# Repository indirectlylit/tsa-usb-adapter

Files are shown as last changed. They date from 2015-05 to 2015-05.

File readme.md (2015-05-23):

# TSA-to-USB Adapter

This project allows computers to communicate with the [Medoc TSA II](http://www.medoc-web.com/products/tsa-ii) using a serial protocol sent over a USB port.

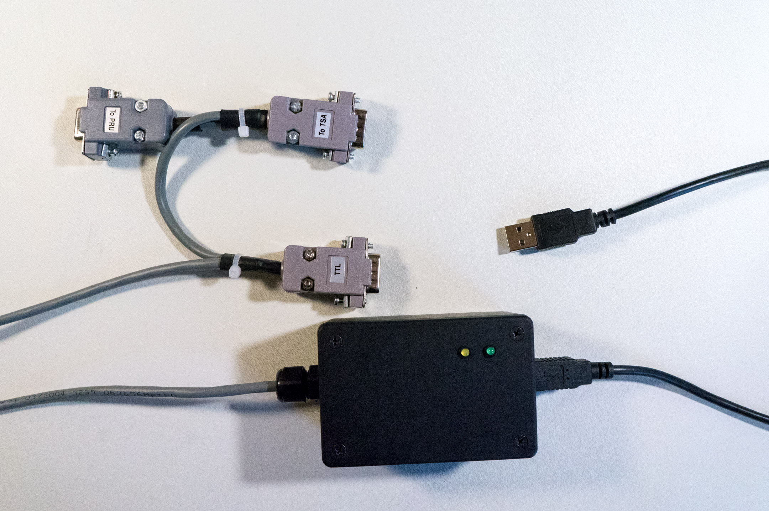
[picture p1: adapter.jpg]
adapter Adapter


## Quick-start

You should also read the the TSA II operation manual (TSA2OperationManual.pdf) to learn how to build TSA programs that send and receive TTL signals.

### Setup

**OSX and Linux**

Plug the adapter into the computer with a USB cord. You may initially get prompts to set up a keyboard or a networking device. Accept the changes and you shouldn't be prompted again.

To verify that the device is available:

* Open the Terminal
* run `ls /dev | grep usb`
* this should return one tty port, for example `/dev/tty.usbmodem411`.

**Windows**

Plug the adapter into the computer with a USB cord. In tests on Windows 7, the computer automatically searched for and installed drivers with no additional work needed.

To verify that the device is available:

* Open the Device Manager
* Look for an entry in the tree: Ports (COM & LPT) > Arduino Micro (COM*N*)

If the drivers did not install successfully in the prior step, you may need to install them manually. For help, try following [these instructions](https://learn.sparkfun.com/tutorials/pro-micro--fio-v3-hookup-guide#installing-windows).

### TSA Software

Open the Hardware Settings dialog in the TSA software to make sure communication is working. Here you can send and receive test pulses.

*NOTE - While the Medoc TSA purports to accept TTL pulse inputs, we have not been able to get it to work.*

### LED feedback

* plug in to computer - green LED will turn on
* `connect()` from the computer - green LED will flash once
* `trigger()` a TTL pulse from the computer - yellow LED will flash once
* receive a TTL pulse from the TSA - yellow LED will flash twice

## Programming in MATLAB

Note that MATLAB will not see the adapter unless it is plugged in when MATLAB starts.

You'll need access to *matlab/TSAAdapter.m* in your program.

### API

**`tsa = TSAAdapter()`**

Constructor - returns a new TSA object. This only needs to be done once at the beginning of your program.

**`tsa.connect()`**

Establish a connection with the adapter. This only needs to be done once at the beginning of your program.

**`tsa.trigger()`**

Send a TTL pulse to the TSA. *NOTE - While the Medoc TSA purports to accept TTL pulse inputs, we have not been able to get it to work.*

**`tsa.check()`**

Return `1` (true) if a TTL pulse was sent by the TSA since the last time `check()` was called; return `0` (false) otherwise. If multiple pulses are sent, `check()` will still only return a `1`.

**`tsa.disconnect()`**

Drop the connection with the adapter. This is optional, as the connection will be automatically dropped when your script ends.

### Example

Basic usage is as follows:

```
>> tsa = TSAAdapter()
>> tsa.connect()
>> tsa.trigger()  % sends a pulse to the TSA
>> tsa.check()    % has a pulse been received since last check?
false
>> tsa.check()
false
>> tsa.check()
true
>> tsa.check()
false
>> tsa.disconnect()
```

## Programming in Python

These notes only apply if you're writing a program in Python - not MATLAB.

The Python helper requires `pyserial` to be installed. This can be obtained by running `pip install pyserial` from the command-line.

You'll need to import the *python/tsa.py* file into your program.

### API

**`import tsa`**

Import the TSA module. This only needs to be done once at the beginning of your program.

**`tsa.connect()`**

Establish a connection with the adapter. This only needs to be done once at the beginning of your program.

**`tsa.trigger()`**

Send a TTL pulse to the TSA.

*NOTE - While the Medoc TSA purports to accept TTL pulse inputs, we have not been able to get it to work.*

**`tsa.check()`**

Return `True` if a TTL pulse was sent by the TSA since the last time `check()` was called; return `False` otherwise. If multiple pulses are sent, `check()` will still only return `True`.

**`tsa.wait()`**

Block execution until a TTL is sent by the TSA.

**`tsa.disconnect()`**

Drop the connection with the adapter. This is optional, as the connection will be automatically dropped when your script ends.

### Example

Basic usage is as follows:

```
>>> import tsa
>>> tsa.connect()
>>> tsa.trigger()  # sends a pulse to the TSA
>>> tsa.wait()     # this call will block until a pulse is received
True
>>> tsa.check()    # has a pulse been received since last check?
False
>>> tsa.check()
False
>>> tsa.check()
True
>>> tsa.check()
False
>>> tsa.disconnect()
```

## Implementation Details

### Theory of Operation

The TSA can send and receive signals via very simple pulses of electricity, called TTL signals. For example, a pulse could signal the TSA to start a test, or the TSA could send a pulse when the user clicks the mouse. Refer to the TSA operation manual (TSA2OperationManual.pdf) for more information on creating TSA programs that send and receive pulses.

Most personal computers do not have the ability to use raw TTL pulses, so this adapter was made to allow programs (e.g. MATLAB or Python) to interact with the TSA. The adapter works by translating TTL signals to serial port messages and vice-versa. The serial port messages are then sent over a USB cable to the computer.

### Serial Protocol

The MATLAB and Python helper libraries implement the logic described below. However, you may be interested in implementing the logic differently; for example if more precise timing is required, then it might be implemented inside a thread (Python) or using event-driven callbacks (MATLAB). It can also be implemented in another programming language.

With the adapter plugged into the computer, have your program or terminal program open a serial port on `/dev/tty.usbmodem411` at 9600 bps.

The adapter communicates with the computer via a simple pair of messages:

* To instruct the adapter to send a pulse to the TSA, send a `*` character over the serial port from the computer.
* When the TSA sends a pulse, a `#` character will be sent from the adapter to the computer over the serial port.

Writing programs to read and write serial port messages is straightforward, and libraries are available in most languages. You can also use a serial terminal program like [CoolTerm](http://freeware.the-meiers.org/) or [screen](https://embeddedfreak.wordpress.com/2008/08/12/using-gnu-screen-to-debug-your-serial-port/) to experiment with the serial port without writing any code.

### Hardware

The adapter is built around an Arduino-compatible microprocessor board, the [SparkFun Pro Micro](https://www.sparkfun.com/products/12640). More information about how it's put together is contained in the *hardware* directory and the *readme.md* file there.

## Copyright

Written and built by Devon Rueckner for [Carissa Cascio at the Vanderbilt University Medical Center](http://www.casciolab.com/).

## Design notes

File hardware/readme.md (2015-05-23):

# Files

* *model.skp* is a [Sketchup](http://www.sketchup.com/) file, used to find dimensions and locations for the board and enclosure cutouts. *model.pdf* is an export of this file.
* *schematic.fzz* is a [Fritzing](http://fritzing.org/) file with the circuit schematic. *schematic.pdf* is an export of this file.
* *firmware.ino* is a text file containing the source code. It can be uploaded to the chip over USB using either the [Arduino IDE](http://arduino.cc/en/main/software) or from the command line using [Ino](http://inotool.org/).
* *bom.pdf* is the bill of materials.

# Circuit notes

The following components are not included in the schematic:

1. The USB receptacle's metal shielding is connected to ground through a 1MΩ resistor and a 10nF capacitor.
2. Another capacitor is placed between Gnd and Vcc.

Also, note that the resistors and capacitors are not included in the bill of materials.

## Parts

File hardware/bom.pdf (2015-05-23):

Quantity | Part | Desc
| Mouser
1 | 645-558-0201-003F | Green LED
1 | 645-558-0301-003F | Yellow LED
2 | 538-22-23-2021 | 2-pos Male Header
1 | 538-22-23-2031 | 3-pos Male Header
1 | 538-22-23-2041 | 4-pos Male Header
2 | 538-50-57-9502 | 2-pos Female Cnctr
1 | 538-50-57-9503 | 3-pos Female Cnctr
1 | 538-50-57-9504 | 4-pos Female Cnctr
1 | 38-08-50-0113-CT | 100x crimp terminals
1 | 523-MUSBD11130 | Panel-mount USB-B
1 | 546-1591XXLBK | Enclosure
also, various resistors & capacitors; see schematic.pdf and readme.md
| SparkFun
1 | 12640 | Pro Micro - 5V/16MHz
2 | 115 | Female headers
2 | 116 | Male headers
1 | 13244 | 6" USB Micro-B Cable
1 | 512 | 6' USB A to B Cable
1 | 08619 | ProtoBoard
| McMaster-Carr
1 | 69915K47 | Cable Gland
2 | 91249A107 | Machine screw
2 | 92295A100 | Thread-forming screw

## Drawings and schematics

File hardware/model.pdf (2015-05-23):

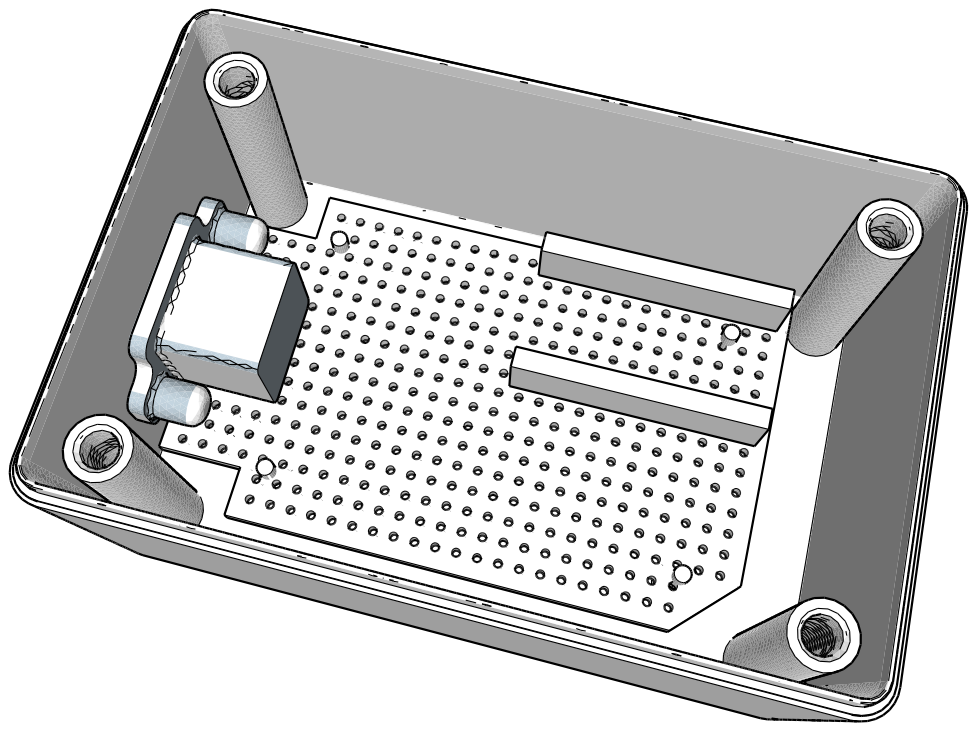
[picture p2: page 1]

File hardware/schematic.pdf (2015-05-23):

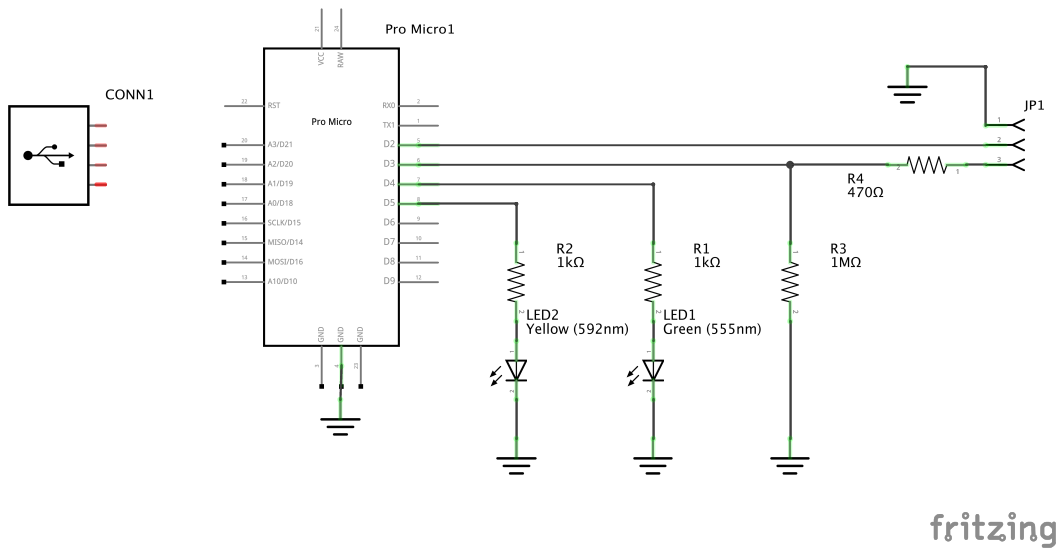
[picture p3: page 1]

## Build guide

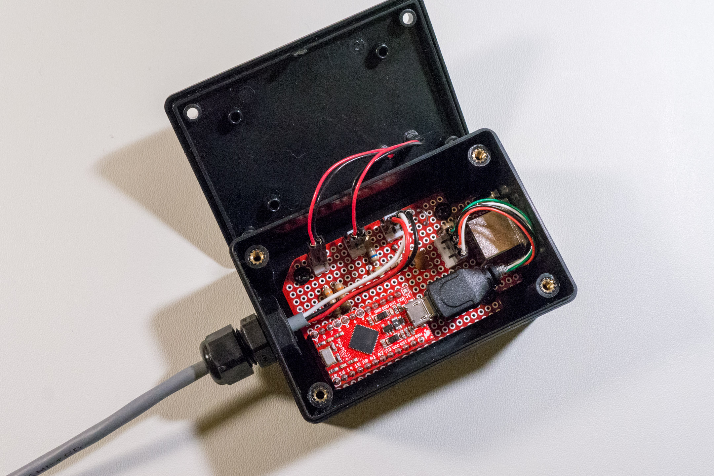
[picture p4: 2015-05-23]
hardware/assembly.jpg

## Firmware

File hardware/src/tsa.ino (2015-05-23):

/*
 *** USAGE
 *
 * This program provides a serial interface adapter to the Medoc TSA-II.
 *
 * When connected to a serial port, it will communicate at 9600 baud.
 * To instruct the TSA to start, send a single '*' character (with no line break).
 * To receive output from the TSA, listen for a '#' character.
 *
 * The status LED will blink:
 *  - 4x when the device first starts
 *  - 3x when the TSA was instructed to start
 *  - 2x when output was received from the TSA
 *  - 1x if an unknown command or character is received
 *
 *
 *** NOTES
 *
 * See the Medoc TSA-II FAQ (http://www.medoc-web.com/support/faq)
 *
 *  TTL input option:
 *    The TSA can be started by an external ±5V, 100-2000msec trigger.
 *    The trigger must be set to External in the CoVAS program algorithm.
 *
 *  TTL output option:
 *    TTL output is a ±5V, duration 50-3000msec pulse (set via Utility-»Setup).
 *    TTL output must be enabled in the CoVAS program algorithm.
 *
 * The '±' part is probably an error.
 *
 *
 *** COPYRIGHT
 *
 * Written by Devon Rueckner for Carissa Cascio
 * Vanderbilt University Medical Center
 * 2015
 *
 */


// I/O pins
#define TSA_OUTPUT_PIN  2  // to TSA-II TTL Out
#define TSA_INPUT_PIN   3  // to TSA-II TTL In
#define STATUS_PIN      4  // green LED indicator
#define ACTIVITY_PIN    5  // yellow LED indicator

// magic character for signaling
#define TRIGGER_CHAR    '#'
#define CONNECT_CHAR    '!'

// `setup` runs once when you press reset or power on.
void setup() {
    // initialize
    pinMode(TSA_OUTPUT_PIN, INPUT);
    pinMode(TSA_INPUT_PIN, OUTPUT);
    pinMode(STATUS_PIN, OUTPUT);
    pinMode(ACTIVITY_PIN, OUTPUT);
    Serial.begin(9600);

    // indicate a successful initialization
    digitalWrite(STATUS_PIN, HIGH);
}

// `receivedPulse` returns true only for a 50-3000ms pulse
bool receivedPulse() {
    unsigned long start = millis();

    do {
        // check if the pulse has ended
        if (!digitalRead(TSA_OUTPUT_PIN)) {
            // make sure the pulse was longer than 50ms
            return millis() - start > 50;
        }
    } while (millis() - start < 3000);

    // the pulse lasted longer than 3000ms
    // wait for the pulse to end and return.
    while(digitalRead(TSA_OUTPUT_PIN));
    return false;
}

// `sendTriggerPulse` sends a 200ms pulse to the TSA
void sendTriggerPulse() {
    digitalWrite(TSA_INPUT_PIN, HIGH);
    delay(200);
    digitalWrite(TSA_INPUT_PIN, LOW);
}

// `blink` flashes an LED n times
void blink(int pin, int nBlinks, bool leaveOn) {
    for (int i = 0; i < nBlinks; i++) {
        digitalWrite(pin, HIGH);
        delay(200);
        digitalWrite(pin, LOW);
        delay(200);
    }
    digitalWrite(pin, leaveOn);
}

// `loop` runs repeatedly
void loop() {

    // check if the TSA appears to be sending a signal
    if (digitalRead(TSA_OUTPUT_PIN)) {
        // wait for the pulse to end
        bool pulsed = receivedPulse();
        // if we got a valid pulse, send a signal back
        if (pulsed) {
            Serial.print(TRIGGER_CHAR);
            blink(ACTIVITY_PIN, 2, false);
        }
    }

    // check if we received a start command
    if (Serial.available() > 0) {
        // read the incoming byte:
        char cmd = Serial.read();
        // trigger command
        if (cmd == TRIGGER_CHAR) {
            sendTriggerPulse();
            blink(ACTIVITY_PIN, 1, false);
        }
        else if (cmd == CONNECT_CHAR) {
            blink(STATUS_PIN, 1, true);
        }
        else {
            // received an unknown command
            blink(STATUS_PIN, 2, true);
        }
    }
}
